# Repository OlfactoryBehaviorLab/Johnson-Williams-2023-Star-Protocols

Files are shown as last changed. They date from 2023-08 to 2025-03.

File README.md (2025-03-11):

# Protocol for Quantifying the Odor Detection Threshold of Mice
# Johnson and Williams, et al., 2023


## https://star-protocols.cell.com/protocols/3043
Scripts and Design files required for the protocol described in the Johnson and Williams, et al., 2023 publication in STAR Protocols

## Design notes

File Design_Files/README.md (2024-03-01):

# 2D and 3D Designs for the Dewan Lab

OdorPort

Collection of 2D and 3D designs for custom components used in the Olfactory Behavior Lab at Florida State University.

3D Files are supplied as stl files for 3D printing purposes.
2D files are supplied as PDF part drawings. Any components not 3D printed will lack an associated stl file. The materials for those 2D drawings are descibed in [Johnson and Williams, 2023](https://star-protocols.cell.com/protocols/3043)

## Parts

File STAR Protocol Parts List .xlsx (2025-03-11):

Part | Discription | Part number | Manufacture # | Vendor | Manufacture
RIG
Rig Frame | ** | ** |  | 80 / 20
Water Custom Panels | ** | ** |  | FRED &TANG
Flow Meter Custom Panels | ** | ** |  | FRED &TANG
Flow Meter Custom Panels | ** | ** |  | FRED &TANG
Flow Meter 10--Vaccuum | AVANTOR MASTERFLEX (VWR LLC) Masterflex Variable-Area Flowmeter with Valve, Direct Reading, Aluminum Fittings, 150-mm Scale; 10 LPM Air | 50-196-1140 | MFLX32003-14 | Fisher Scientific | AVANTOR MASTERFLEX
Flow Meter 2.5 w/ knob--clean air | AVANTOR MASTERFLEX (VWR LLC) Masterflex Variable-Area Flowmeter with Valve, Direct Reading, Brass Fittings, 150-mm Scale; 2.5 LPM Air | 50-196-1143 | MFLX32004-10 | Fisher Scientific | AVANTOR MASTERFLEX
Flow Meter 2.5 w/o know--exhaust | Masterflex® Variable-Area Flowmeter without Valve, Direct-Reading, Brass Fittings, 150-mm Scale; 2.5 L/min Air | MFLX32001-10 | MFLX32001-10 | Avantor (VWR) | AVANTOR MASTERFLEX
1/4 in Female Connectors NPT | Female Adapter: Nylon, Push-to-Connect x FNPT, For 1/4 in Tube OD, 1/4 in Pipe Size, Black, 10 PK | 1PEL6 | 3014 56 14 | Grainger
1/4 in tubing--blue | 5/32″ ID x 1/4″ OD, 3/64″ Wall Thickness, Cut to Length (1000' Standard Length) Polyurethane Tube Blue, 123 Max psi, 95 Hardness | 48651442 | PT0404-1000B | MSC | COILHOSE PNEUMATICS
1/4 in tubing--red | 5/32″ ID x 1/4″ OD, 3/64″ Wall Thickness, Cut to Length (1000' Standard Length) Polyurethane Tube | 48651681 | PT0404-1000TR | MSC | COILHOSE PNEUMATICS
1/4 in tubing--black | 5/32″ ID x 1/4″ OD, 3/64″ Wall Thickness, Cut to Length (1000' Standard Length) Polyurethane Tube Black, 123 Max psi, 95 Hardness | 48651509 | PT0404-1000K | MSC | COILHOSE PNEUMATICS
1/4 in tubing--yellow | GRAINGER APPROVED Tubing: Polyurethane, ID 5/32 in, OD 1/4 in, 100 ft Lg, Yellow | 1CTG5 | 1CTG5 | Grainger
1/8 in tubing--blue | 1/16″ ID x 1/8″ OD, 1/32″ Wall Thickness, Cut to Length (2,500' Standard Length) Polyethylene Tube Blue, 150 Max psi | 48655187 | PE021-2500B | MSC | COILHOSE PNEUMATICS
1/8 in tubing--black | 3/32″ ID x 1/8″ OD, 1/64″ Wall Thickness, Cut to Length (500' Standard Length) Nylon 11 Tube Black, 852 Max psi, 78 Durometer Hardness | 74203712 | 36004 | MSC
1/4 in Y connector PTC | Wye Union: Nylon, Push-to-Connect x Push-to-Connect x Push-to-Connect, Black, Imperial, 10 PK | 1DDR5 | 3140 56 00 | Grainger
Manual Needle valve 1/4 in PTC | SMC Speed Control Valve: Tube, 1/4 in Valve Port Size, 1/4 in Valve Tube Size, In Valve Flow | 4DGV3 | AS2052F-07 | Grainger
1/4 in Y union PTC | Wye Union: Nylon, Push-to-Connect x Push-to-Connect x Push-to-Connect, Black, Imperial, 10 PK | 1DDR5 | 3140 56 00 | Grainger
vaccuum regualtor | SMC Vacuum Regulator: 1/4 in Vacuum Inlet Size, Push to Connect, 140 lpm Max Flow Rate, IRV | 30J548 | IRV10-N07BG | Grainger
Organic filter | ** |  |  | Fred & TANG
restek filter | Super-Clean Gas Filters Replacement (Charcoal) Hydrocarbons Filter, Ultra High Capacity | 22030 |  | Restek
restek base | Super-Clean Baseplate Single Position Baseplate for One Cartridge Filter, 1/8" Brass Fittings | 22025 |  | Restek
1/8-1/4 in Unqual union PTC connector | Unequal Union: Nylon, Push-to-Connect x Push-to-Connect, For 1/8 in x 1/4 in Tube OD, Black, 10 PK | 1PEW2 | 3106 53 56 | Grainger
HAM-LET Ball Vavle | Ball Valve: 1/4 in Pipe Size, Std, 300 psi CWP Max. Pressure, -40 to 400 F, Toggle Hangle | 3ZVX3 | H-1280-B-N-1/4-A | Grainger
Air and Nitrogne Gauges | Ashcroft 30052.5 Commercial Gauge with Back Connection, 0 to 30 psi, 2-1/2" Dial | EW-68008-03 |  | Cole-Parmer
Air Regulator | SPEEDAIRE Compressed Air Regulator: Brass, 1/4 in NPT, 15 cfm, 400 psi Max Op Pressure, Nonrising | 4ZM06 |  | Grainger
Air Tank Regulator | Airgas Single Stage Brass 0-25 psi General Purpose Cylinder Regulator CGA-590 | Y11215A590-AG |  | AirGas
Nitrogen Tank Regulator | Airgas Single Stage Brass 0-25 psi General Purpose Cylinder Regulator CGA-580 | Y11215A580-AG |  | AirGas
1/4 in NPT to PTC connector | Male Adapter: Brass, Push-to-Connect x MNPT, For 1/4 in Tube OD, 1/8 in Pipe Size, 18 mm Overall Lg | 36X026 | KQ2H07-34AS | Grainger
Vavle and Gauge Custom Panel | ** |  |  | FRED &TANG
1/8 in Equal union PTC connector | Union: Nylon, Push-to-Connect x Push-to-Connect, For 1/8 in x 1/8 in Tube OD, Black, 10 PK | 1PEV2 | 3106 53 00 | Grainger
Zero Dead Space Electronic Needle Vavle | EIVU-Z-ENS | EIVU-Z-ENS |  | Clippard
Zero Dead Space fitting | Headless 1/4-28 Flatbottom Fitting, 1/8" OD | ZDVF-18 |  | Clippard
3 way-dual synchronous soleinoid Valve | Dual 3-way isolation valve | SH360T042 |  | NResearch
OLFACTOMETER
1/8 in elbow fitting connector | Male Elbow: Brass, Push-to-Connect x MNPT, For 1/8 in Tube OD, 1/8 in Pipe Size | 36X076 | KQ2L01-34AS | Grainger
1L/SLPM Mass Flow Controller | Mass Controller, 0 - 1 SLPM, Display | MC-1SLPM-D/5M, 5IN, GAS: Air |  | AliCat
100SCCM Mass Flow Controller | Mass Controller, 0 - 100 SCCM, Display | MC-100SCCM-D/5M, 5IN, GAS: Air |  | AliCat
MFC Power cord-- | Power Adapter - 24 VDC, 1 Amp (Worldwide) | PVPS24U |  | AliCat
custom MFC power cord
barb fitting-- Tygon to Manifold | Barb Fittings Zero Dead Volume | FITM331 |  | NResearch
4 Position, 3 normally close 1 normally open manifold | Nresearch-3 NC, 1 NO 2-way Inline Isolation Valve | 225T081 |  | NResearch
4 Position Normally closed Manifold | 4x2-way NC Inline Isolation Valve | 225T082 |  | NResearch
1/8 in black ferrle/yellow nut | Super Flangeless™ Ferrule Tefzel™ (ETFE), 1/4-28 Flat-Bottom, for 1/8" OD Yellow - 10 Pack | P-359X |  | Idex
big Teflon Tubing | Teflon Tubing .062 in I.D., .125 in O.D., Inert(PTFE) | TBGM110 |  | NResearch
1/8 in Manual Needle Valve PTC
Nitrogen manifold plug | Plug 1/4-28 PTFE | FITM128 |  | NResearch
Two piece fitting set | Two Piece fitting set 1/4-28, 0.36x0.62 PCTFE | 252P109-50 |  | NResearch
small Teflon tubing | Teflon Tubing .036 in I.D., .062 in O.D., Inert(PTFE) | TBGM109 |  | NResearch
Amber Glass Vials
Silicon/Teflon Septum w/ Cap
Teensy to computer Cable
Teensy connector board | PJRC Teensy USB Board with Header Pins |  |  | PJRC
Controller Board
Vial board
Dummy Vial Board
2 Position Jumper Pin | 2 (1 x 2) Position Shunt Connector Black Closed Top 0.100" (2.54mm) Tin | S9000-ND | STC02SYAN | DigiKey | Sullins Connector Solutions
Female Molex Connector | Socket Contact Tin 20-24 AWG Crimp Power | WM1837-ND | 430300007 | DigiKey | Molex
Male Molex Housing | 2 Rectangular Connectors - Housings Receptacle Black 0.118" (3.00mm) | WM1845-ND | 436450200 | DigiKey | Molex
small cable ribbon | CBL RIBN 10COND 0.05 GRAY 5'; Flat Ribbon Cable Gray 10 Conductors 0.050" (1.27mm) Flat Cable 5.0' (1.52m) | MC10G-5-ND | 3365/10 300SF | DigiKey | 3M
small cable ribbon connector | CONN RCPT 10P IDC 26-28AWG GOLD; 10 Position Rectangular Receptacle Connector IDC Gold 26-28 AWG | MKC10A-ND | 89110-0101 | DigiKey | 3M
Power Cable
On/Off Switch
3 in machine screw
Board stand-offs | BRD SPT SNAP LOCK NYLON 1/4" | RP426-ND | LCBS-4-01 | DigiKey | Essentra Components (https://www.digikey.com/en/supplier-centers/essentra-components)
Custom acrylic shield | ** |  |  | FRED &TANG
ARDUINO/COMPUTER
Arduino plastic casing | ** |  |  | FRED&TANG
Arduino custom panel | ** |  |  | FRED&TANG
BNC cable rigs | Connector Nut For BNC and TNC Connectors | A97566-ND | 1-1634816-0 | DigiKey | TE Connectivity AMP Connectors
BNC cable | CBL ASSY BNC PLUG-PLUG RG58C 6'; Cable Assembly Coaxial BNC to BNC RG-58C 72.0" (1.8m) 6.0' | 501-1021-ND | 2249-C-72 | DigiKey | Pomona Electronics (https://www.digikey.com/en/supplier-centers/pomona-electronics)
BNC Cable | CBL ASSY BNC PLUG RG58C 36"; Cable Assembly Coaxial BNC to BNC RG-58C 36.00" (914.40mm) | 501-1018-ND | 2249-C-36 | DigiKey | Pomona Electronics (https://www.digikey.com/en/supplier-centers/pomona-electronics)
ZDS Electronic needle valve Controller Box | ** |  |  | FRED &TANG
4 position black cable | CABLE MOD FLAT 4COND BLACK 100';4 Conductor Modular Straight Cable Black 100' (30.5m) | A0042R-100-ND | AT-K-26-4-B/100 | DigiKey | Assmann WSW Components (https://www.digikey.com/en/supplier-centers/assmann-wsw-components)
LCD Screen Ardunio board | LCD MOD 32DIG 16X2 TRANS YLW/GRN; Character Display Module Transflective 5 x 8 Dots STN - Super-Twisted Nematic LED - Yellow/Green Serial 80.00mm x 36.00mm x 25.50mm | 27977-ND | 27977 | DigiKey | Parallax Inc. (https://www.digikey.com/en/supplier-centers/parallax)
small single pin wires with housing |  |  |  |  | Polulo
Arduino Board | ARDUINO MEGA2560 ATMEGA2560; ATmega2560 Arduino Mega2560 AVR® ATmega AVR MCU 8-Bit Embedded Evaluation Board | 1050-1018-ND | A000067 | DigiKey | Arduino (https://www.digikey.com/en/supplier-centers/arduino)
Arduino power? | AC/DC WALL MOUNT ADAPTER 12V 12W | 102-3432-ND | SWI12-12-N-P6 | DigiKey | CUI Inc. (https://www.digikey.com/en/supplier-centers/cui)
Arduino to computer cable
Breakout Board | 2x20 0.1" Header IDC40 Breakout Board | BRK2X20-L-DIN |  | Winford
wiring | ** |  |  | FRED&TANG
40 position ribbon Cable | IDC CBL - HHKC40S/AE40G/HHKC40S; 40 Position Cable Assembly Rectangular Socket to Socket 3.00' (914.40mm) | H3CCS-4036G-ND | H3CCS-4036G | DigiKey | Assmann WSW Components (https://www.digikey.com/en/supplier-centers/assmann-wsw-components)
#2-56 nut | Hex Nut: #2-56 Thread, 3/16 in Hex Wd, 1/16 in Hex Ht, Steel, Not Graded, Zinc Plated, 100 PK (https://www.grainger.com/product/GRAINGER-APPROVED-Hex-Nut-2-56-Thread-2FE43) | 2FE43 | 325040-PG | Grainger
BEHAVIORAL BOX
Lick ciruit board
#2 mechanical screw 1/2 in | #2-56 Machine Screw, Carbon Steel, 1/2" L, 100 PK | 1ME91 |  | Grainger
metal lick tube
dental wax | Utility Wax Strips HSI Round White 64/Bx | 1008759 |  | Henry Schein
tygon tubing--lick tubes | Tubing: Tygon S3 E-3603, TPE, 1/32 in Inside Dia, 3/32 in Outside Dia, 50 ft Lg, Clear | 22XH28 | ACF00001 | Grainger
60 mL syringe | SYRINGE LUER LOCK 60CC CS100 | 15003-094 | SS-60L | VWR | TERUMO MEDICAL INC. (https://us.vwr.com/store/supplier/id/0000020530/terumo-medical-inc.)
needle to water solinoid connection | Cole-Parmer Adapter, PP, Male Luer Lock to 10-32 thread, 25/pack | EW-45518-84 |  | Cole-Parmer
blunted interlocking needle 21 GA | Blunt Tip Needles with Dispensing Tips, Air-Tite | 89500-304 | NB2112 | VWR | AirTite
water solienoid | 2-way NC Isolation Valve | 161T012 |  | Nresearch
angle bracket micromanipulator | DT100-AB; angle bracket, DT-100 series | 60050000E |  | Siskiyou
micromanipulator | DT3-100; dovetail stage, 12mm travel, XYZ | 62080000E |  | Siskiyou
vaccuum/mfc tygon tubing | Tubing: Tygon S3 B-44-3, TPE, 1/8 in Inside Dia, 3/16 in Outside Dia, 50 ft Lg, Clear | 2LPR9 | AAB00006 | Grainger
barb to NPT--tygon vaccuum to flowmeter | 1/8″ Barb, 1/8 NPT, Nylon Single Barbed Tube Adapter | 48712244 | A2-2BN | MSC
1/2 in pedestal | Ø1" (Ø25.0 mm) Pedestal Posts, 1/4"-20 (M6) Taps | RS05P |  | Thorlabs
pedastal clamp | CF125-P5 - Clamping Fork, 1.24" Counterbored Slot, Universal, 5 Pack | CF125-P5 |  | Thorlabs
Magnetic Base (Top and Bottom) | Complete 3" x 3" Kinematic Base, Top and Bottom Plates, 1/4"-20 Mounting | KB3X3 |  | ThorLabs
Bread Board 12x12 | Aluminum Breadboard 12" x 12" x 1/2", 1/4"-20 Taps | MB12 |  | ThorLabs
light bulb | LED WHITE CLEAR T-1 T/H; White LED Indication - Discrete 12V Radial | LTH3MM12VFR4400-ND | LTH3MM12VFR4400 | DigiKey | Visual Communications Company - VCC (https://www.digikey.com/en/supplier-centers/visual-communications-company)
4 in optical post | 1/2" Optical Post, SS, 8-32 Setscrew, 1/4"-20 Tap, L = 4" | TR4 |  | Thorlabs
2 in pedestal | Ø1" (Ø25.0 mm) Pedestal Posts, 1/4"-20 (M6) Taps | RS2P |  | ThorLabs
Webcam | Generic U19-A Night Vision Webcam 12.0MP, Microphone Built In | JUF4645 |  | Amazon
1/4-20 screw inserts | Knurled Press Insert: Flanged, 1/4-20 Internal Thread Size, 1/2 in Lg, 5/16 in Drill Size, 25 PK | 4ZU39 |  | Grainger
thumb screw inserts | GRAINGER APPROVED Press Insert: Brass, 4-40 Internal Thread Size, 3/16 in Lg, 50 PK | 1GUC6 |  | Grainger
headbar clamps
headbar clamp pin
thumb screw | Thumb Screw: #4-40 Thread Size, Knurled, 18-8 Stainless Steel, Plain, 0.094 in Max Head Ht | 5RA21 | Z2300SS | Grainger
custom headbar
Teflon Odor Port | JF-DR-OP0008 Odor Port, Top |  |  | Max Plank Neuroscience
#2 mechanical screw 3/4 in | #2-56 Machine Screw, Carbon Steel, 3/4" L, 100 PK | 1ME92 |  | Grainger
exhaust fan | FAN AXIAL 80X25.4MM 12VDC WIRE | 381-2335-ND
sound proofing foam | Quiet Barrier® Specialty Composite: 1 1/4 in. thick x 48 in. x 54 in. sheet with PSA |  |  | Soundproof Cow
custom acrylic base plate | ** |  |  | FRED&TANG
1/4-20 set screw | HW-KIT2 - 1/4"-20 Cap Screw and Hardware | HW-KIT2 |  | ThorLabs
#4-40 nut for set screw small | Hex Nut: #4-40 Thread, 1/4 in Hex Wd, 3/32 in Hex Ht, Steel, Not Graded, Zinc Plated, 100 PK (https://www.grainger.com/product/GRAINGER-APPROVED-Hex-Nut-4-40-Thread-2GA51) | 2GA51 | 325080-PG | Grainger
CLEANING
Surgery
screws for head-bar surgeries |  | 000-120 X 1/16th inch | AMS120-1B-25 | Antrin Miniature Specialties
heat therapy pump |  |  | HTP1500 | Kent scientific

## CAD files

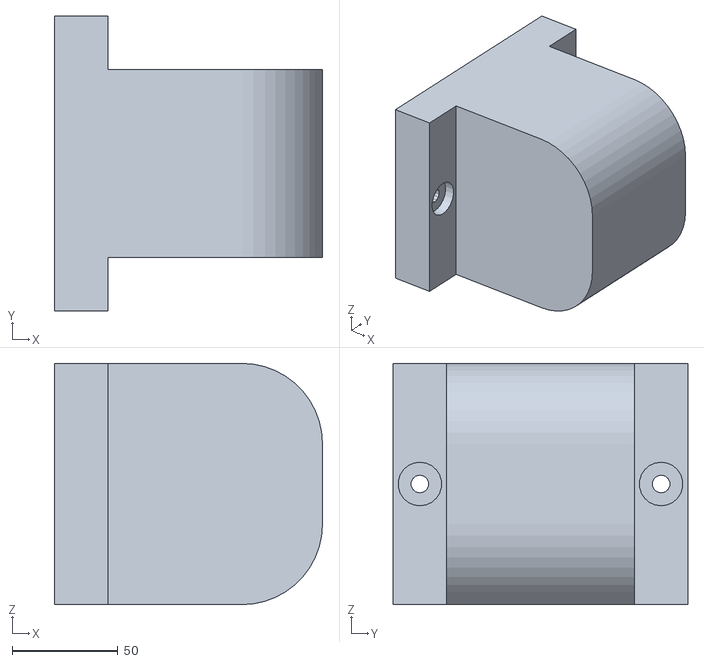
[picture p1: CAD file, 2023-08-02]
Design_Files/Behavioral_Rig_Components/Cleaning_Bottle_Holder/Cleaning Bottle Holder.stl
127.0 x 139.7 x 114.3

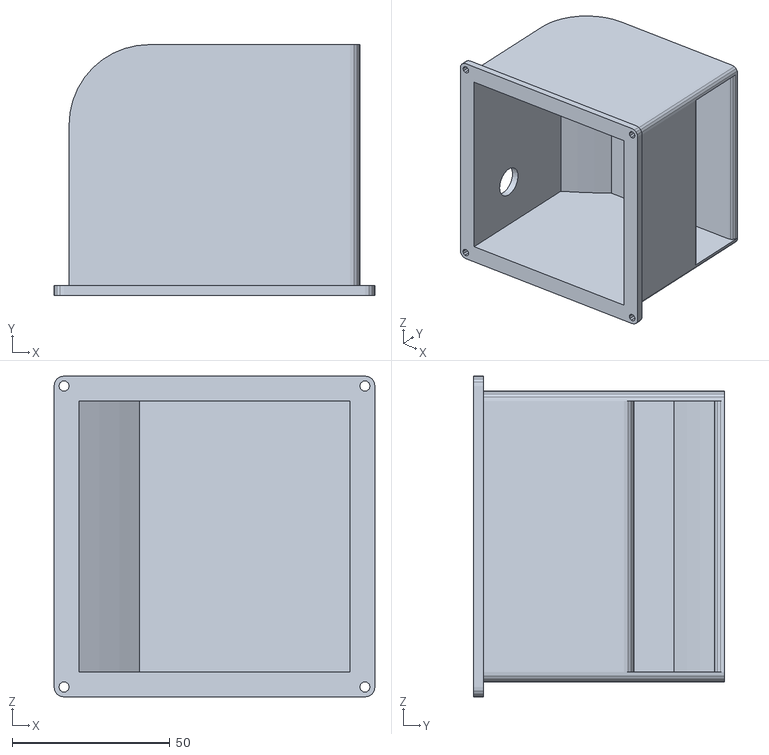
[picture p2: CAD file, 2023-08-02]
Design_Files/Behavioral_Rig_Components/Fan_Exhaust_Cover/FanExhaustCover.stl
101.6 x 79.4 x 101.6

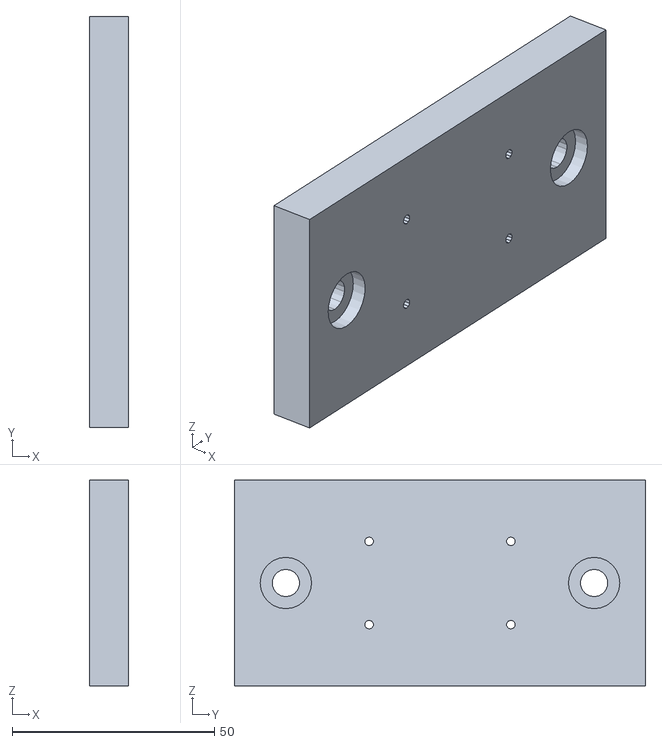
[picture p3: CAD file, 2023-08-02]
Design_Files/Behavioral_Rig_Components/FinalValve_Mount/FinalValveMount.stl
9.52 x 101.6 x 50.8

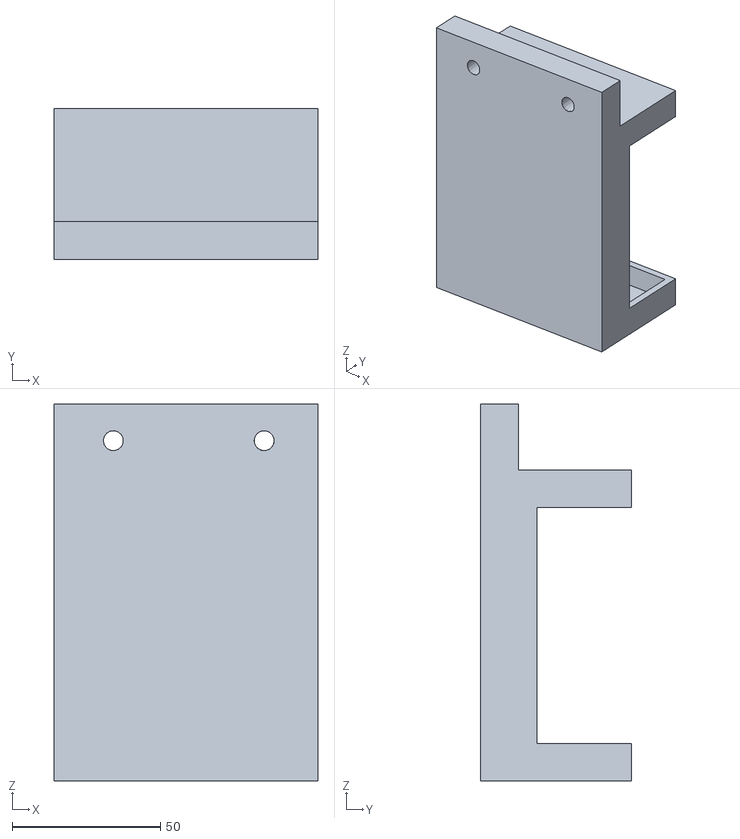
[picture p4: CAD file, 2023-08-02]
Design_Files/Behavioral_Rig_Components/KVM_Holder/KVM Holder RMount.stl
88.9 x 50.8 x 127.0

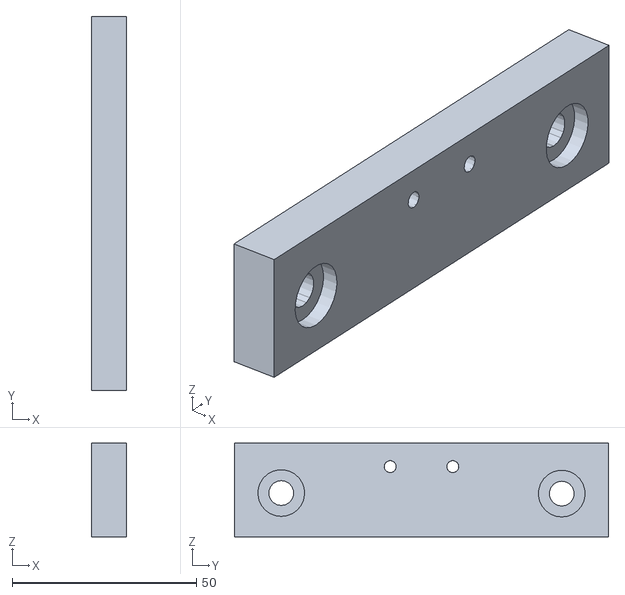
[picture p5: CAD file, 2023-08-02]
Design_Files/Behavioral_Rig_Components/Manual_NeedleValve_Mount/ManualNeedleValveMount.stl
9.52 x 101.6 x 25.4

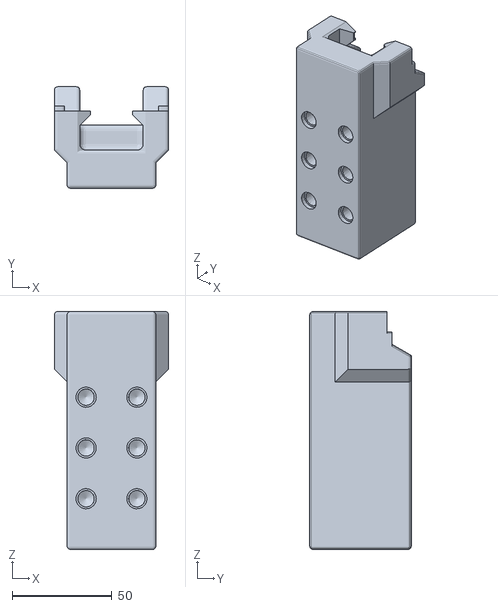
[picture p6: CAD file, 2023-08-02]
Design_Files/Behavioral_Rig_Components/Mouse_Holder/mouse holder.stl
57.2 x 50.8 x 119.1

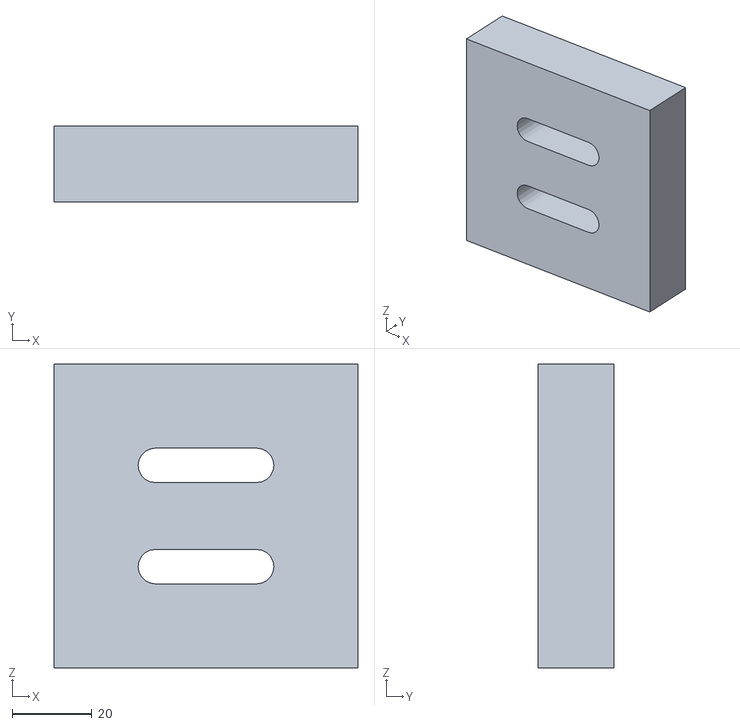
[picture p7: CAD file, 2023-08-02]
Design_Files/Behavioral_Rig_Components/Mouse_Holder_Riser/Mouse Holder Riser.stl
76.2 x 19.0 x 76.2

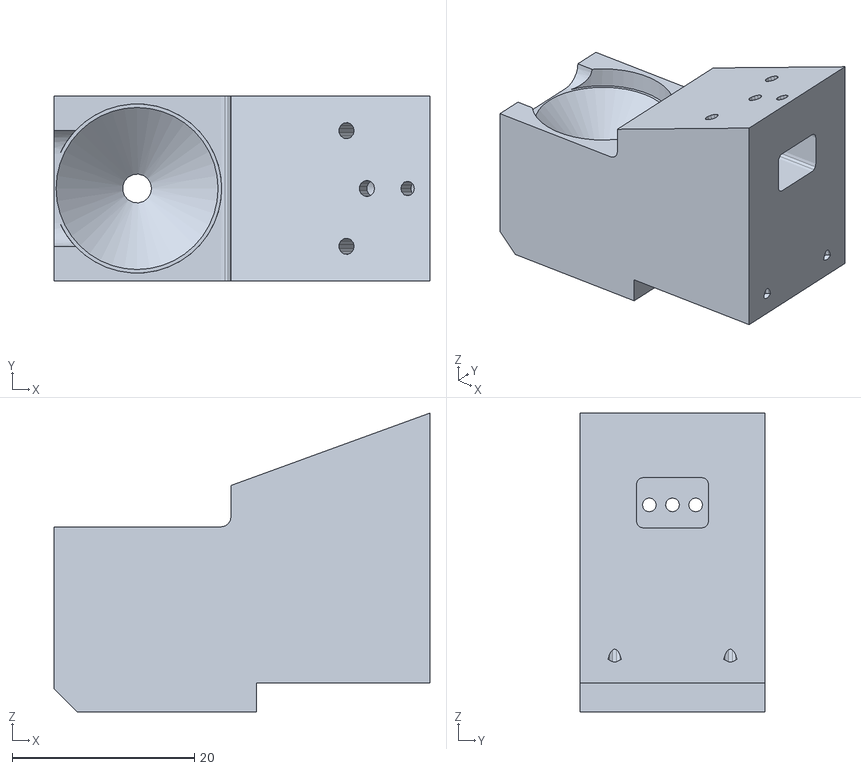
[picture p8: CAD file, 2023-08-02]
Design_Files/Behavioral_Rig_Components/Odor_Port_Base/Odor Port Base.stl
41.3 x 20.3 x 32.8

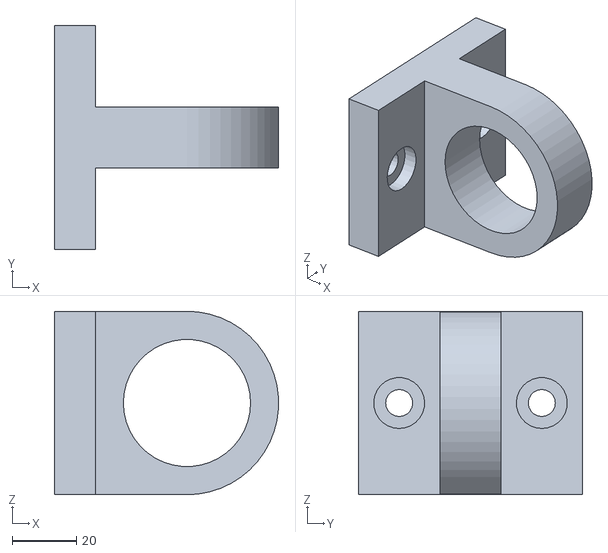
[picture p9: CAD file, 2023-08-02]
Design_Files/Behavioral_Rig_Components/Organic_Filter_Holder/Organic Filter Holder.stl
69.8 x 69.8 x 57.2

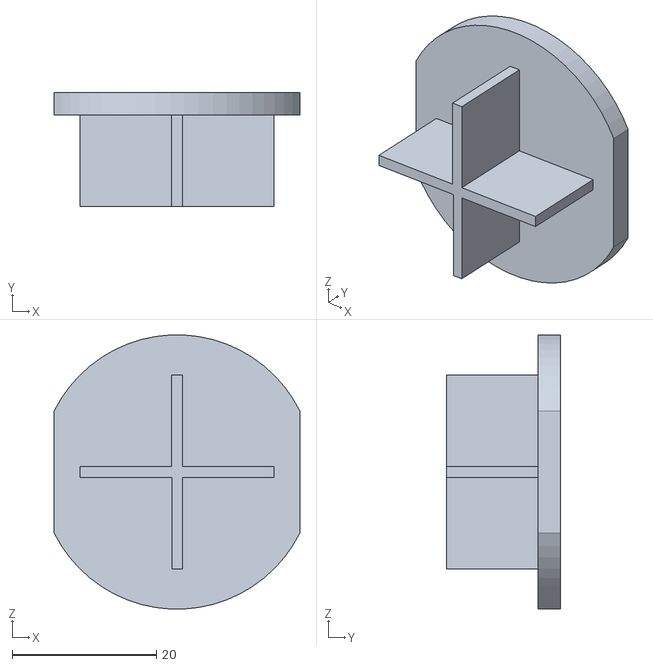
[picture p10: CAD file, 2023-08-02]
Design_Files/Behavioral_Rig_Components/Water_Syringe_Cap/Water Syringe Cap.stl
34.1 x 15.9 x 38.0

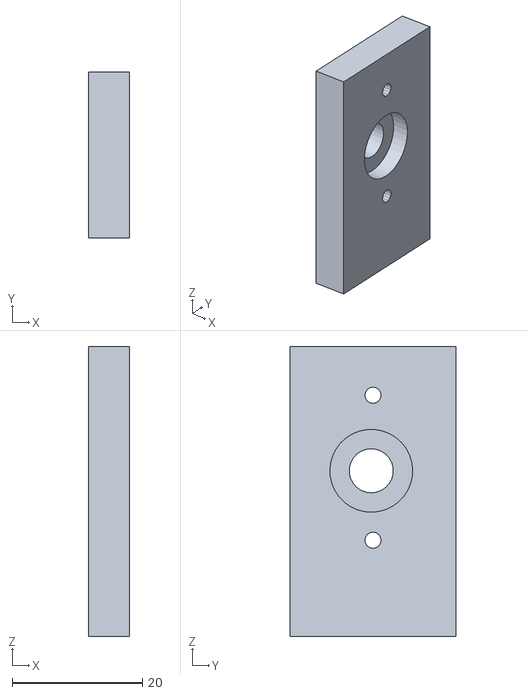
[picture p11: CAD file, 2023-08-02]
Design_Files/Behavioral_Rig_Components/ZeroDeadSpace_ElectronicNeedleValve_Panel/Zero Dead Space Electronic needle valve holder.stl
6.35 x 25.4 x 44.5

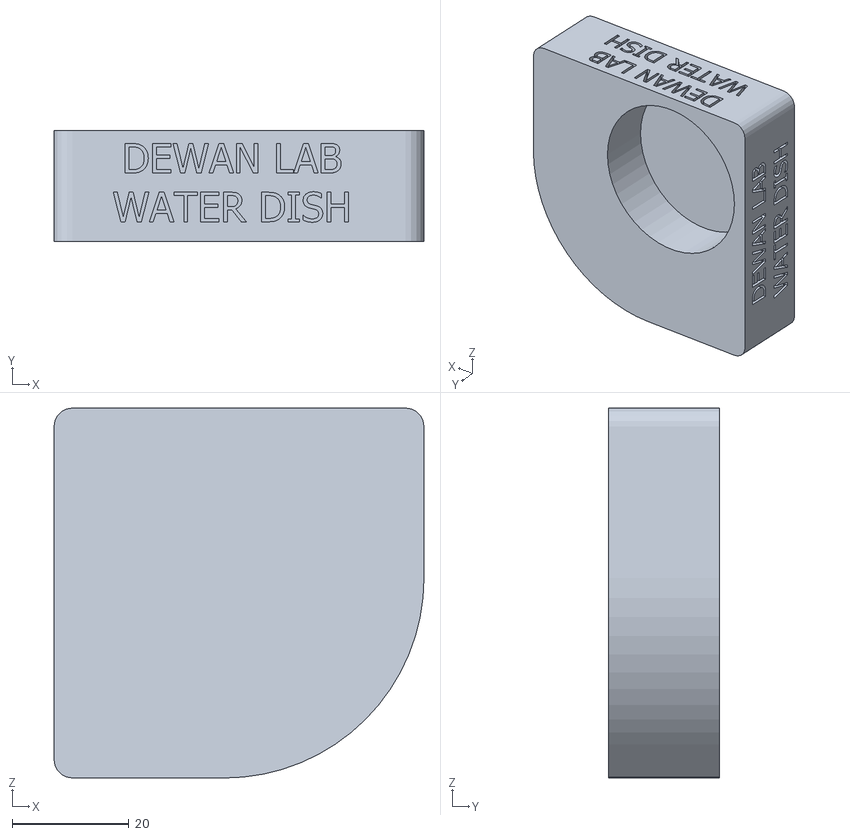
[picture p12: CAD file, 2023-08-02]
Design_Files/General_Components/Water_Dish_Holder/water dish holder.stl
63.5 x 19.0 x 63.5

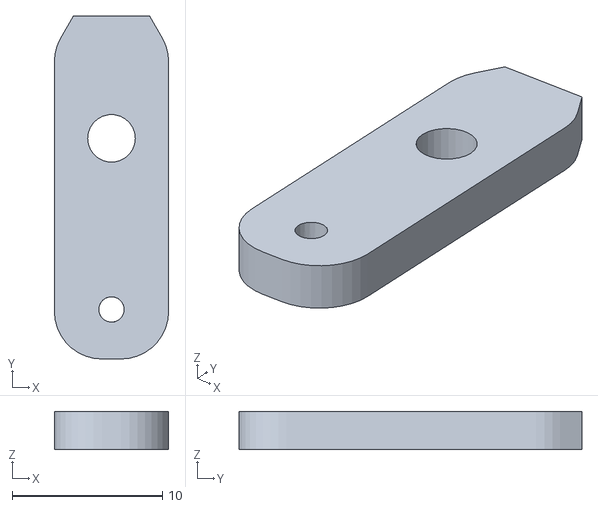
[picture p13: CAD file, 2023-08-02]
Design_Files/Headbar_Components/HEADBAR CLAMP/Headbar clamp.stl
7.62 x 22.9 x 2.54

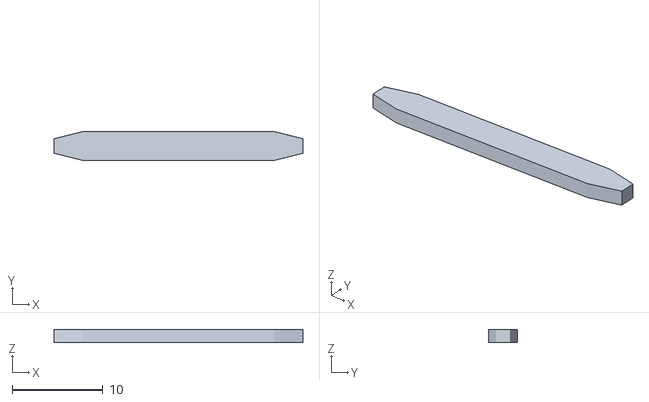
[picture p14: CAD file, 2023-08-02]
Design_Files/Headbar_Components/HEADBAR/Head Bar.stl
27.4 x 3.17 x 1.40

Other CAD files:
Design_Files/Olfactometer_Components/Olfactometer_Manifold_Holder/Olfactometer Manifold Holder.stl
Design_Files/Olfactometer_Components/Olfactometer_Vial_Holder/Vial Holder 4 spaces.stl
Design_Files/Behavioral_Rig_Components/KVM_Holder/KVM Holder LMount.stl
Design_Files/Behavioral_Rig_Components/Mouse_Holder/mouse holder cover.stl
Design_Files/Behavioral_Rig_Components/Odor_Port_Base/Odor Port Base_Side Version.stl

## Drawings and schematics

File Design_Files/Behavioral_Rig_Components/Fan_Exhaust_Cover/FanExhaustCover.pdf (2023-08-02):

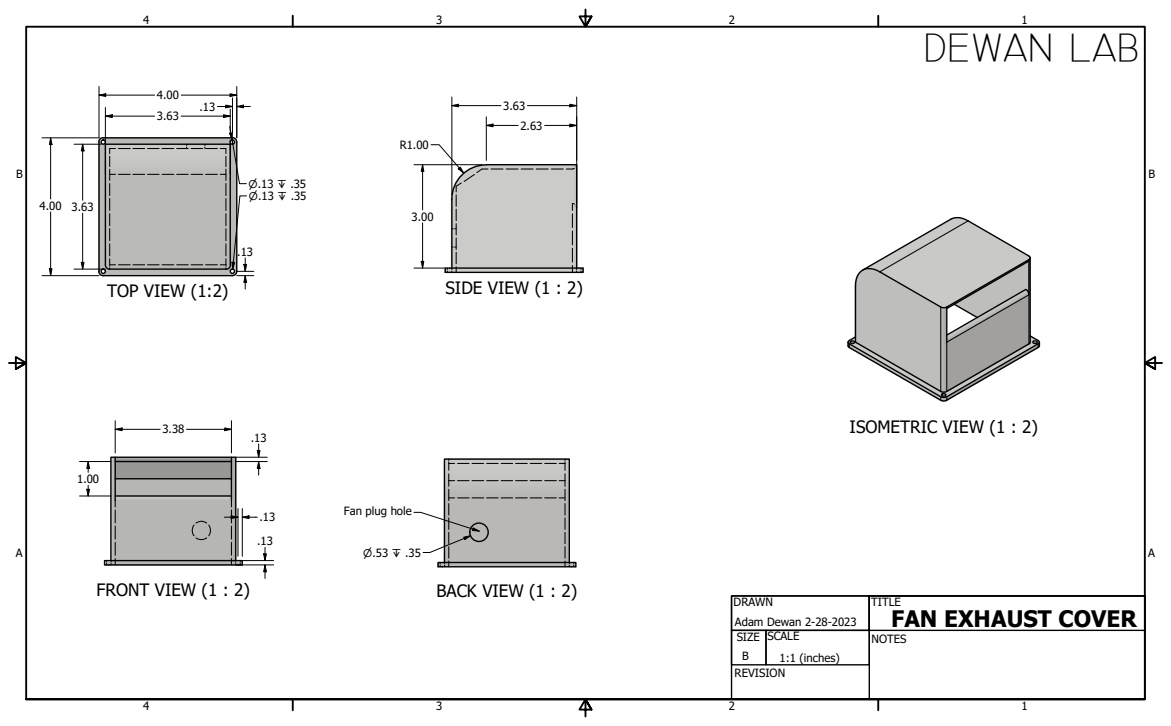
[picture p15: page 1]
TOP VIEW (1:2); SIDE VIEW (1 : 2); FRONT VIEW (1 : 2); BACK VIEW (1 : 2); ISOMETRIC VIEW (1 : 2); DEWAN LAB

Fan plug hole

DRAWN Adam Dewan 2-28-2023 | TITLE FAN EXHAUST COVER

SIZE B | SCALE 1:1 (inches) | NOTES

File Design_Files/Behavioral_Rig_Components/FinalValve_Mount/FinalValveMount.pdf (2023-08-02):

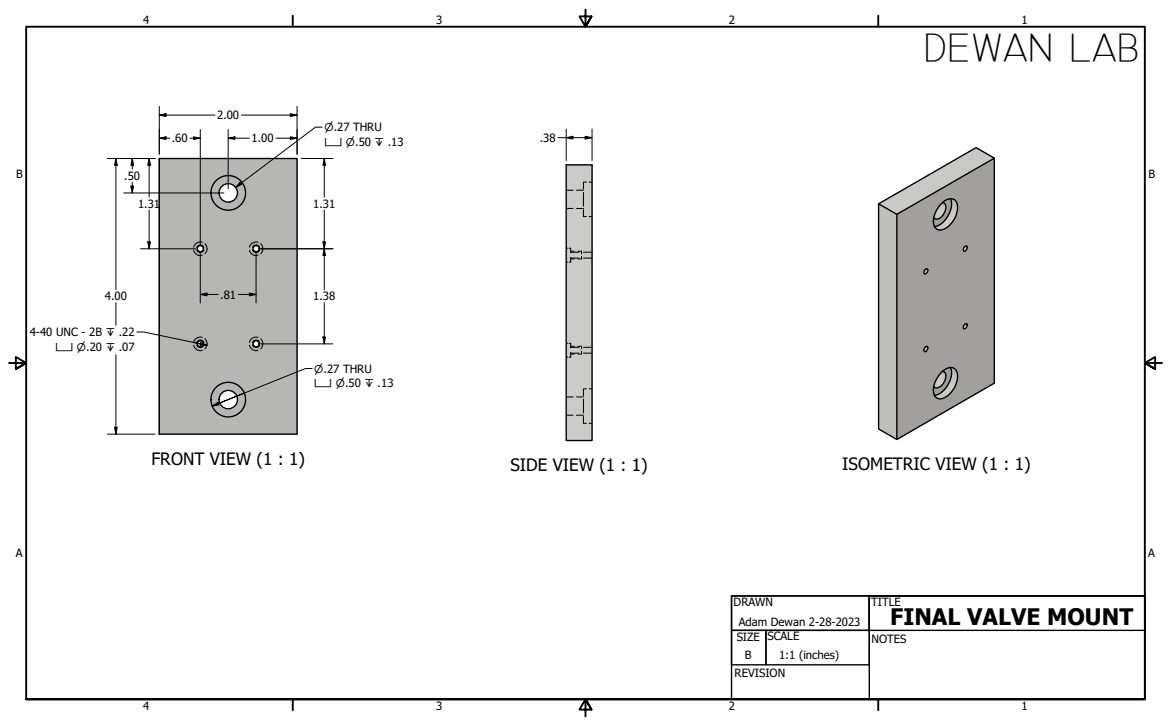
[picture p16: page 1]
FRONT VIEW (1 : 1); SIDE VIEW (1 : 1); ISOMETRIC VIEW (1 : 1); DEWAN LAB; ⌀.27 THRU ⌴ ⌀.50 ↧ .13; 4-40 UNC - 2B ↧ .22 ⌴ ⌀.20 ↧ .07

DRAWN Adam Dewan 2-28-2023 | TITLE FINAL VALVE MOUNT

SIZE B | SCALE 1:1 (inches) | NOTES

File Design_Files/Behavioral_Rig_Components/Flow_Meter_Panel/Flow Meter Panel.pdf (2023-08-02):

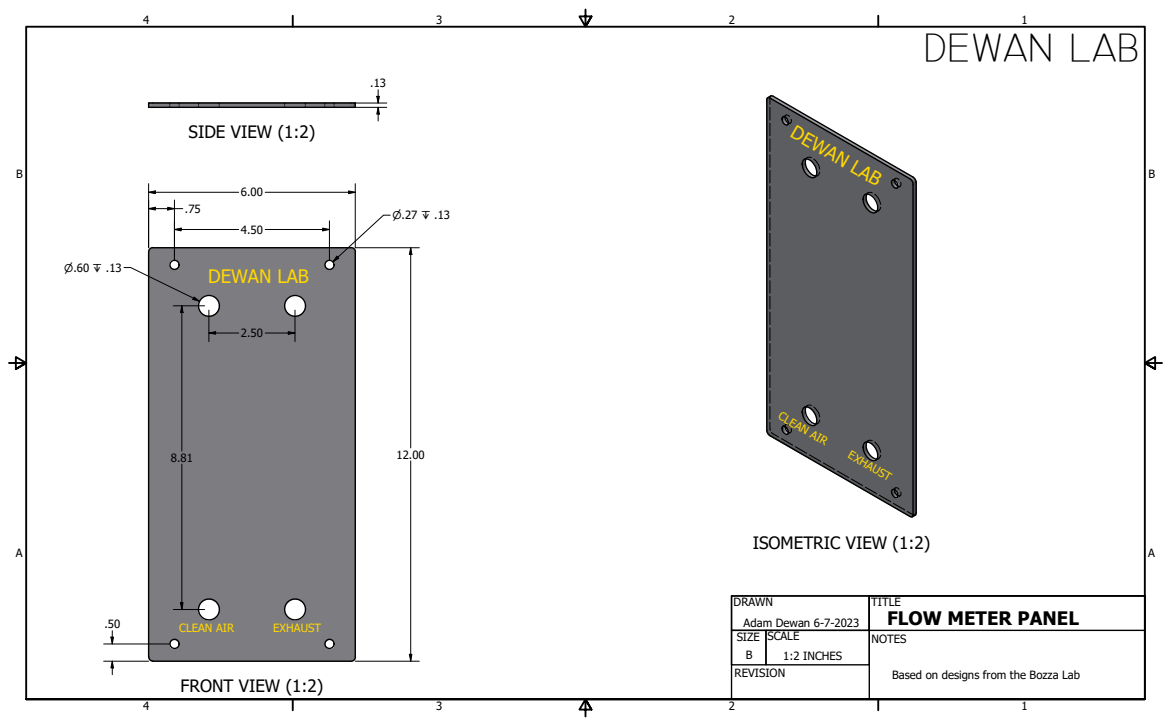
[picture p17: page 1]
SIDE VIEW (1:2); FRONT VIEW (1:2); ISOMETRIC VIEW (1:2); DEWAN LAB; CLEAN AIR; EXHAUST

DRAWN Adam Dewan 6-7-2023 | TITLE FLOW METER PANEL

SIZE B | SCALE 1:2 INCHES | NOTES Based on designs from the Bozza Lab

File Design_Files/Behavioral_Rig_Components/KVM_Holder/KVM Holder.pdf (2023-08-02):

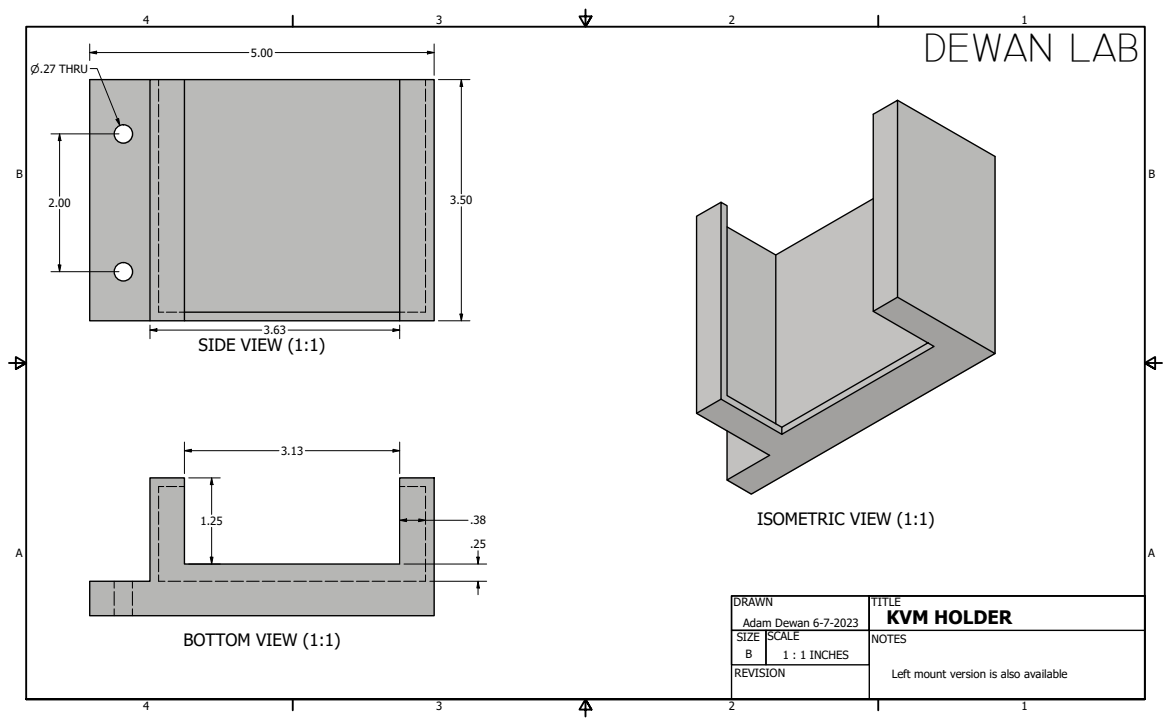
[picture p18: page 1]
SIDE VIEW (1:1); BOTTOM VIEW (1:1); ISOMETRIC VIEW (1:1); DEWAN LAB; ⌀.27 THRU

DRAWN Adam Dewan 6-7-2023 | TITLE KVM HOLDER

SIZE B | SCALE 1 : 1 INCHES | NOTES Left mount version is also available

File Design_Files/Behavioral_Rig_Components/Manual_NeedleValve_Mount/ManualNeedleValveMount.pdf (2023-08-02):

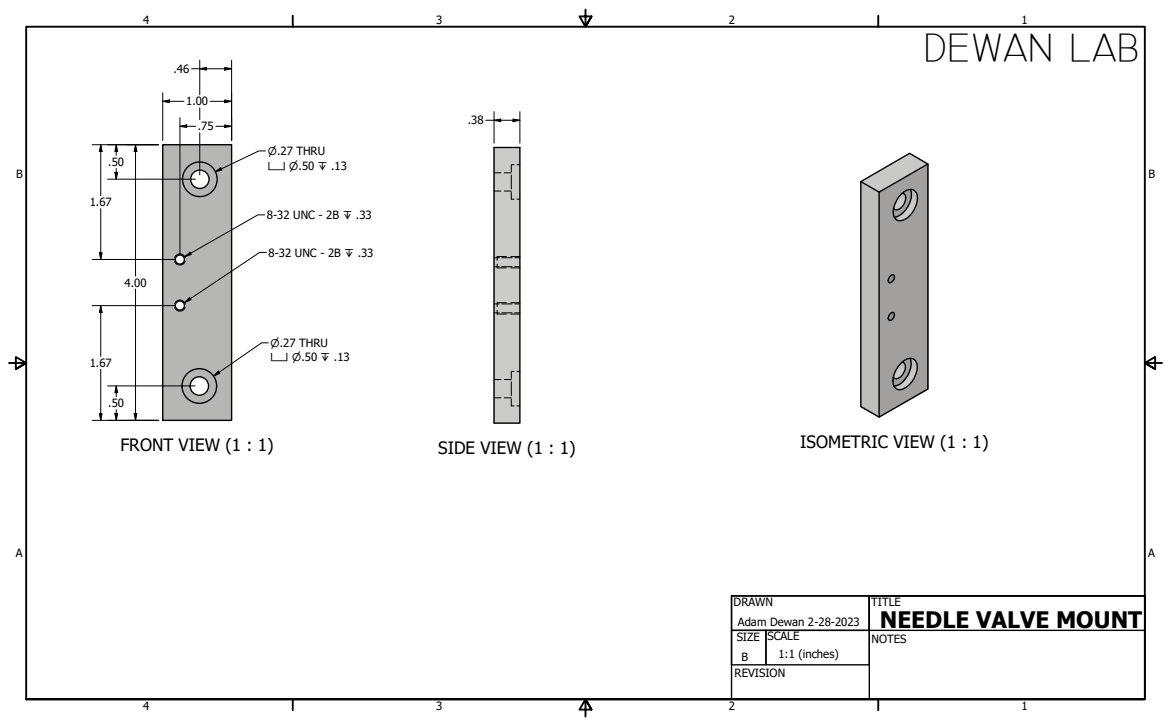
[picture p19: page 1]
FRONT VIEW (1 : 1); SIDE VIEW (1 : 1); ISOMETRIC VIEW (1 : 1); DEWAN LAB; ⌀.27 THRU ⌴ ⌀.50 ↧ .13; 8-32 UNC - 2B ↧ .33

DRAWN Adam Dewan 2-28-2023 | TITLE NEEDLE VALVE MOUNT

SIZE B | SCALE 1:1 (inches) | NOTES

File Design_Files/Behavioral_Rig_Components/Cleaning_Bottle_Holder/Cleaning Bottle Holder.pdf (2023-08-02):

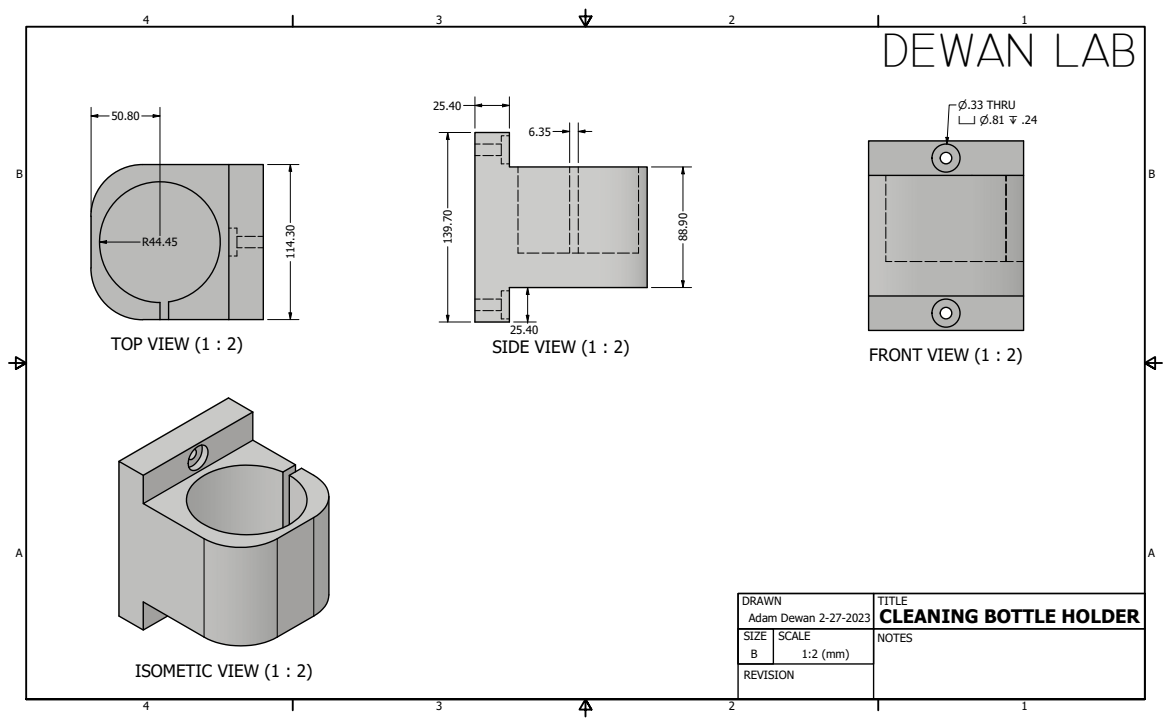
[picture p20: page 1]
TOP VIEW (1 : 2); SIDE VIEW (1 : 2); FRONT VIEW (1 : 2); ISOMETIC VIEW (1 : 2); ⌀.33 THRU ⌴ ⌀.81 ↧ .24; DEWAN LAB

DRAWN Adam Dewan 2-27-2023 | TITLE CLEANING BOTTLE HOLDER

SIZE B | SCALE 1:2 (mm) | NOTES

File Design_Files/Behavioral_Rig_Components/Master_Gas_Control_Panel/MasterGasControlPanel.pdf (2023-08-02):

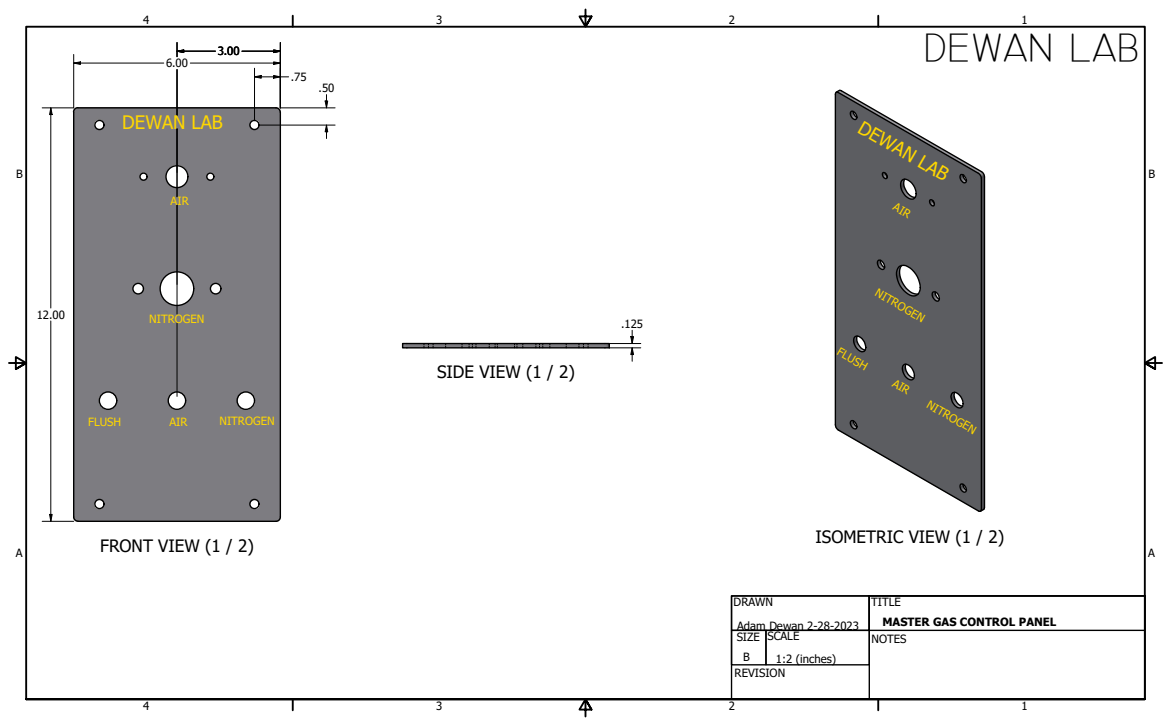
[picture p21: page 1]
FRONT VIEW (1 / 2); SIDE VIEW (1 / 2); ISOMETRIC VIEW (1 / 2); DEWAN LAB

DRAWN Adam Dewan 2-28-2023 | TITLE MASTER GAS CONTROL PANEL

SIZE B | SCALE 1:2 (inches) | NOTES

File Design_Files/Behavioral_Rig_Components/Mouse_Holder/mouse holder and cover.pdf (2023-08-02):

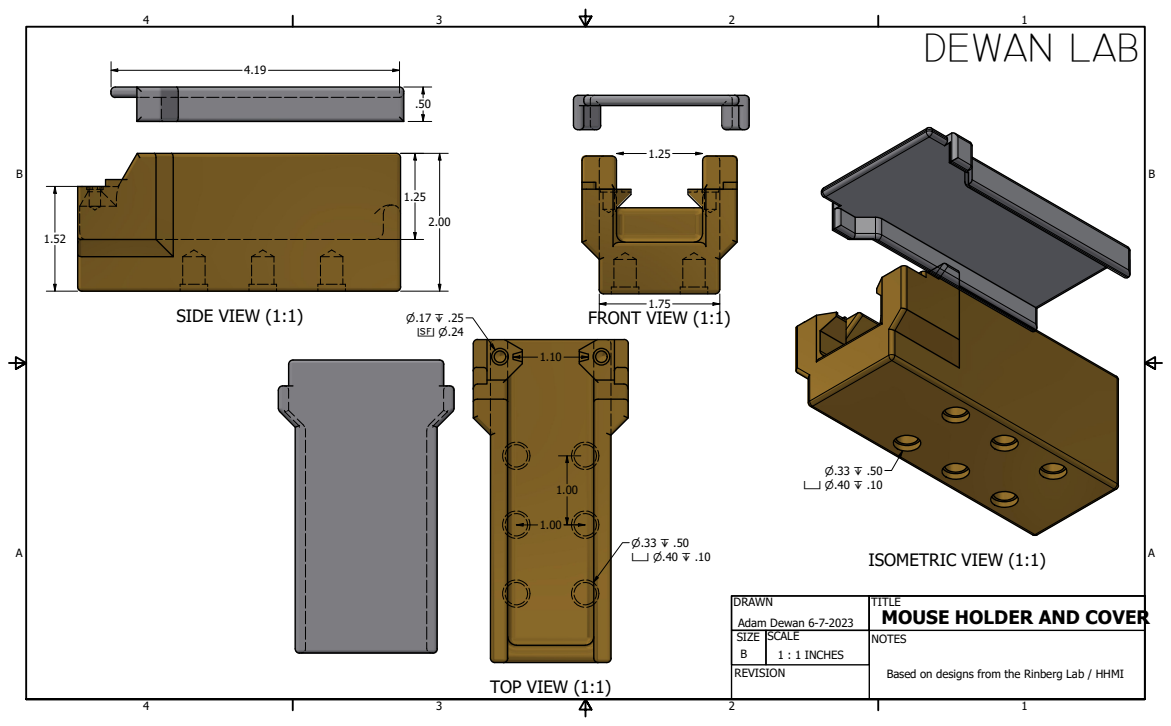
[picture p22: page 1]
SIDE VIEW (1:1); TOP VIEW (1:1); FRONT VIEW (1:1); ISOMETRIC VIEW (1:1); DEWAN LAB; Adam Dewan 6-7-2023; MOUSE HOLDER AND COVER

DRAWN | TITLE

SIZE B | SCALE 1 : 1 INCHES | NOTES Based on designs from the Rinberg Lab / HHMI

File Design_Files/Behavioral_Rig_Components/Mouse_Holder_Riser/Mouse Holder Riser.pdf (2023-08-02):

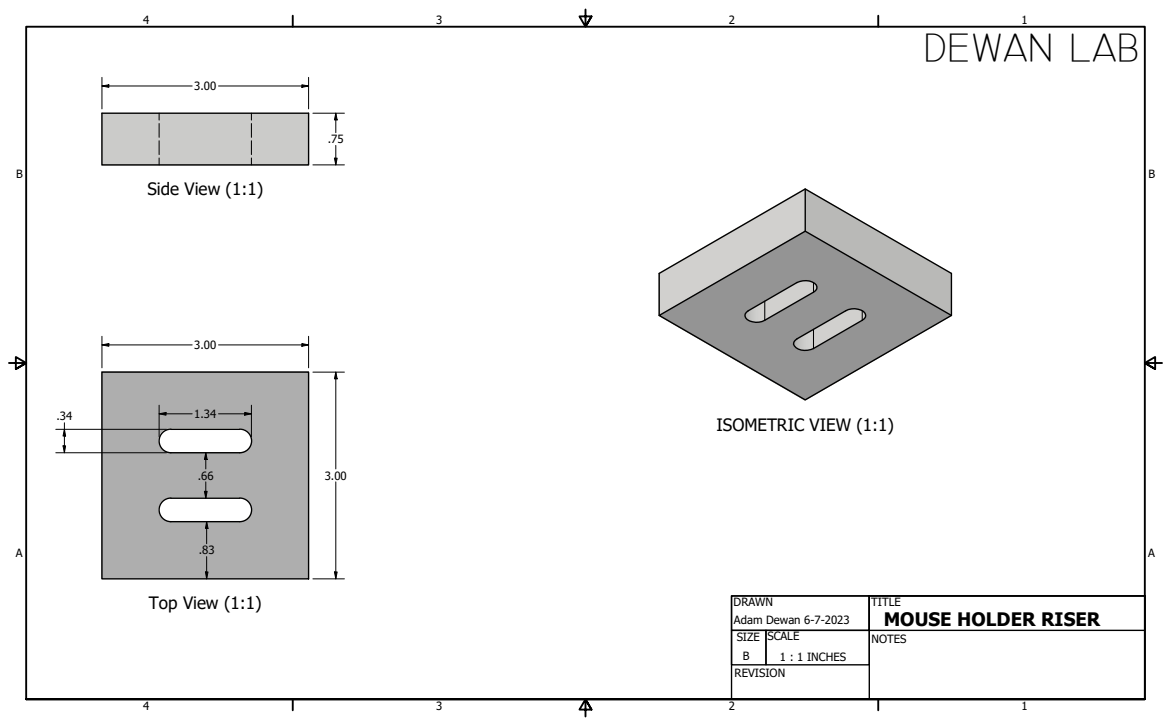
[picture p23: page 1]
Side View (1:1); Top View (1:1); ISOMETRIC VIEW (1:1); DEWAN LAB

DRAWN Adam Dewan 6-7-2023 | TITLE MOUSE HOLDER RISER

SIZE B | SCALE 1 : 1 INCHES | NOTES

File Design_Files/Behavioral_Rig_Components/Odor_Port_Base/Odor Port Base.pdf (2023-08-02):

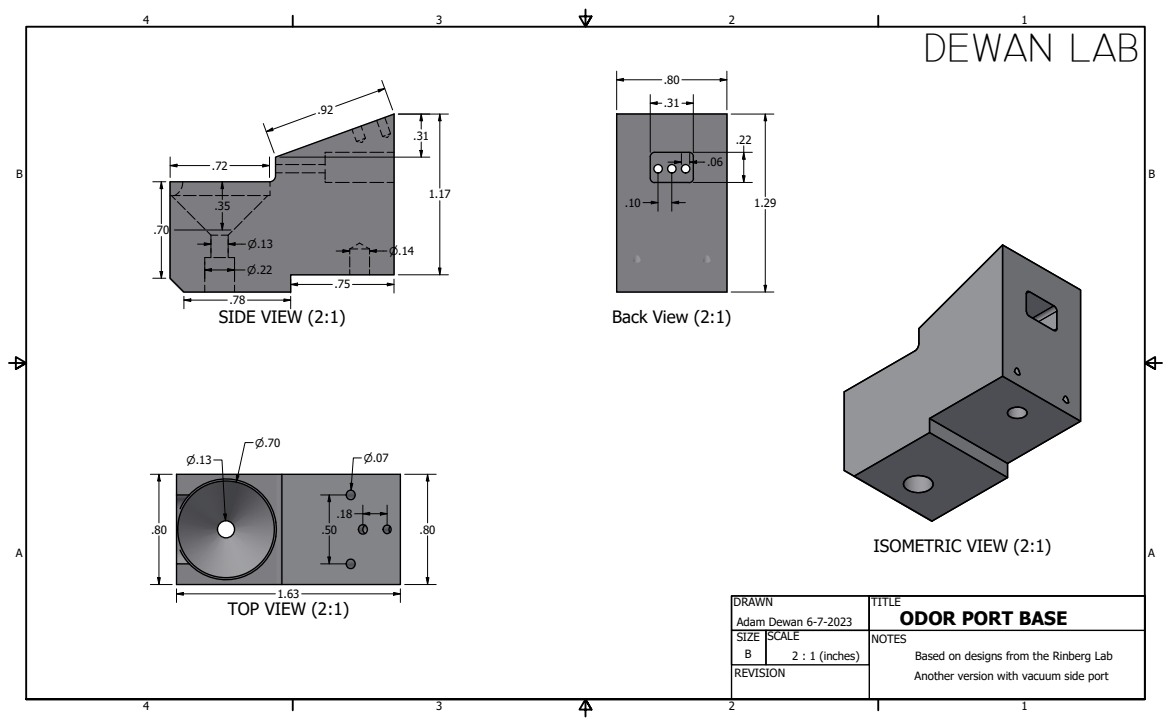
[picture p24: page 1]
SIDE VIEW (2:1); TOP VIEW (2:1); Back View (2:1); ISOMETRIC VIEW (2:1); DEWAN LAB

DRAWN Adam Dewan 6-7-2023 | TITLE ODOR PORT BASE

SIZE B | SCALE 2 : 1 (inches) | NOTES Based on designs from the Rinberg Lab Another version with vacuum side port

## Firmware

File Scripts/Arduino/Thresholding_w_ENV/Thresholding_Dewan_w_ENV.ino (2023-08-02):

// include the library code:
#include <SPI.h>
#include <C:\Voyeur_protocols_and_files\Arduino\libraries\voyeur_timer_lib.pde>
#include <C:\Voyeur_protocols_and_files\Arduino\libraries\ioFunctions_external_timers.pde>
#include <C:\Voyeur_protocols_and_files\Arduino\libraries\voyeur_serial_stream_tools.pde>
#include <C:\Voyeur_rig_config\arduino_rig_config.h>

#define INITIALGO 0
#define GO 1
#define NOGO 2

#define PASSIVE 4
#define PASSIVEREWARDED 3
#define POSITIVE 1
#define NEGATIVE 0
#define FV 3
#define TRIAL_LED CUE3
#define THREEMISSED_LED CUE4
#define FVSYNC DIGITAL7

//=======================
// Set the protocol name
char protocolName[] = "ThresholdingENV"; // should be less than 20 characters
//=======================

//=======================
// PARAMETERS OF TASK
unsigned long waterdur = 60;
unsigned long waterdur2 = 60;
unsigned long trialdur = 1000000;
unsigned long sniffmaxdelay = 0;
unsigned long rchoice = INITIALGO;
unsigned long fvdur = 0;
unsigned long grace_period = 0;
unsigned long firststim = 0;
unsigned long iti = 5000;
//unsigned long lickfirst = 1;
unsigned long fvonset = 0;
unsigned long lickStartTime = 0;



//event to be transmitted back
unsigned int result = 0;
unsigned long paramsgottime = 0;
unsigned long starttrial = 0;
unsigned long endtrial = 0;
unsigned long firstlick = 0;
unsigned long firstcorrectlick = 0;
unsigned int no_sniff = 0;
unsigned long fvOnTime = 0;
unsigned long vialOnTime = 0;
unsigned long laserontime = 0;

// variables
uint8_t idx = 0, fv_routine_timer = 255, laser_routine_timer = 255, led_timer = 255;
uint16_t lickindex;  // lick index
int blocks;
bool trialdone = false, lastsent = false, enableblocks = false, maskon = false, ledMaskwFV = true,trialwait = false;
volatile bool trig_stop = false; bool beam1state, beam2state;
// state of the state machine
int code = 0, state = 0, trig_laser_multi_sniff = 0;
unsigned long temp1 = 0, inh_onset = 0, lastlickstamp = 0, lastlick1 = 0, lickcheckpoint=0;
int last_sniffndx = -1, cur_sniffndx = 0;
unsigned long nextpulsedelay = 0;
int treadmill_response_type = 0, rewards_given = 0;

//clean count iterates how many times the program will attempt to clean the mouse within a single session.
//lastCleanTime is the last time the cleaning iteration was started.

char buffer[128];
char *argv[8];
//bool received_params = 0;
//char laserdur[20], laseramp[20];

int step_num = 0;










void setup() {
  pinMode(LED_PIN, OUTPUT); // Green LED on the front
  pinMode(TRIGGER1, OUTPUT); // Pulse generator ch. 1 trigger
  pinMode(TRIGGER2, OUTPUT); // Pulse generator ch. 2 trigger
  pinMode(SOLENOID1, OUTPUT);
  pinMode(SOLENOID2, OUTPUT);
  pinMode(SOLENOID3, OUTPUT);
  pinMode(SOLENOID4, OUTPUT);
  pinMode(SOLENOID5, OUTPUT);
  pinMode(SOLENOID6, OUTPUT);
  pinMode(SOLENOID7, OUTPUT);
  pinMode(SOLENOID8, OUTPUT);
  pinMode(DIGITAL1,OUTPUT);
  pinMode(DIGITAL2,OUTPUT);
  pinMode(DIGITAL3,OUTPUT);
  pinMode(DIGITAL4,OUTPUT);
  pinMode(DIGITAL5,OUTPUT);
  pinMode(DIGITAL6,OUTPUT);
  pinMode(DIGITAL7,OUTPUT);
  pinMode(DIGITAL8,OUTPUT);
  pinMode(DIGITAL9,OUTPUT);  
  pinMode(DIGITAL10,OUTPUT);
  pinMode(DIGITAL11,OUTPUT);
  pinMode(DIGITAL12,OUTPUT);
  pinMode(CUE1, OUTPUT);
  pinMode(CUE2, OUTPUT);
  pinMode(CUE3, OUTPUT);
  pinMode(CUE4, OUTPUT);
  pinMode(CUE5, OUTPUT);
  pinMode(CUE6, OUTPUT);
  pinMode(CUE7, OUTPUT);
  pinMode(CUE8, OUTPUT);
  pinMode(ADC_PIN, OUTPUT);
  pinMode(DAC1_PIN, OUTPUT);
  pinMode(DAC2_PIN, OUTPUT);
  pinMode(TEENSY_PIN, OUTPUT);

  digitalWrite(LED_PIN, LOW);
  digitalWrite(TRIGGER1, LOW);
  digitalWrite(TRIGGER2, LOW);
  digitalWrite(SOLENOID1, LOW);
  digitalWrite(SOLENOID2, LOW);
  digitalWrite(SOLENOID3, LOW);
  digitalWrite(SOLENOID4, LOW);
  digitalWrite(SOLENOID5, LOW);
  digitalWrite(SOLENOID6, LOW);
  digitalWrite(SOLENOID7, LOW);
  digitalWrite(SOLENOID8, LOW);
  digitalWrite(DIGITAL1,LOW);
  digitalWrite(DIGITAL2,LOW);
  digitalWrite(DIGITAL3,LOW);
  digitalWrite(DIGITAL4,LOW);
  digitalWrite(DIGITAL5,LOW);
  digitalWrite(DIGITAL6,LOW);
  digitalWrite(DIGITAL7,LOW);
  digitalWrite(DIGITAL8,LOW);
  digitalWrite(DIGITAL9,LOW);
  digitalWrite(DIGITAL10,LOW);
  digitalWrite(DIGITAL11,LOW);
  digitalWrite(DIGITAL12,LOW);
  digitalWrite(CUE1, LOW);
  digitalWrite(CUE2, LOW);
  digitalWrite(CUE3, LOW);
  digitalWrite(CUE4, LOW);
  digitalWrite(CUE5, LOW);
  digitalWrite(CUE6, LOW);
  digitalWrite(CUE7, LOW);
  digitalWrite(CUE8, LOW);
  digitalWrite(LED_PIN, LOW);
  digitalWrite(ADC_PIN, HIGH);
  digitalWrite(DAC1_PIN, HIGH);
  digitalWrite(DAC2_PIN, HIGH);
  digitalWrite(TEENSY_PIN, HIGH);

  //=======================
  // prep ANALOG inputs
  analogReference(DEFAULT);
  //=======================

  //=======================
  // prep SPI for AD control
  startSPI();
  //=======================

  //=======================
  // initialize the SERIAL communication
  Serial.begin(115200);
  //Serial.begin(921600);

  //Serial.println("* Monitor System ready *");
  //=======================

  //=======================
  // initialize SERIAL for LCD
  Serial1.begin(19200); 
  Serial1.write(0x0c); // clear the display
  delay(10);
  Serial1.write(0x11); // Back-light on
  Serial1.write(0x80); // col 0, row 0
  Serial1.print("*CleanThresholding   Dewan Lab*");
  delay(20);
  //    Serial1.print(0x94, BYTE); // col 0, row 0
  //    Serial1.print("MODE 0");
  //=======================

  // Pulse generator communication
  Serial2.begin(115200);
  setupVoyeurTimer(); //setup and start ms timer (From: voyeur_timer_lib.pde) (THIS DEFINES TOTALMS).

  // setup buffer sizes
  setupBuffers(400,1,20,50);  //(ioFunctions)(unsigned int sniffbuff, unsigned int treadmillbuff, unsigned int lickbuff, unsigned int trigbuff)

  // recording of both sniff and velocity
  // first two args are analog channels' pins, 1 indicates ONLY SNIFF ON, 3 indicates both on.
  setupAnalog(0,1,1); 

  // start analog acquisition
  start_analog_timer(); //(ioFunctions).
  // start lick recording timer.
  // first arg. is the beam break pin, second is the amount of ms to wait. 0 = every ms
  startLick(BEAM1,BEAM2);//(ioFunctions).
  lickOn(3, 0); // 3 - turn on both lick pins, 0 is frequency (every ms). (ioFunctions).
  recordsniffttl = true;

  // Init done
  digitalWrite(LED_PIN, HIGH);
}

//===================================================================================================
void loop() {  //BREAKS TO HERE

  //===================================================================================================
  //================ State machine goes here===========================================================
  unsigned long timenow = totalms; //copy this to register from volatile.



  switch (state) {

  case 0: //waiting for initialization of trial
    break;



  case 1: // state was changed to 1 via controller (serial).
//    if((timenow-endtrial) < iti)  // wait for the inter-trial interval to be over (difference between last trial and the current time)
//      break;
//    else{
      vialOnTime = timenow;
      state = 2;
//    }
    break;

  case 2: // Wait for odor to reach max
    if((timenow-vialOnTime) < 900)  // 
      break;
    else{
      state = 3;
      digitalWrite(TRIAL_LED,HIGH); //Turn on Trial Light
      starttrial = timenow;
    }
    break;


  case 3:  // FINAL VALVE     If the final valve gets turn on, turn on the final valve for fdur time and mark the time

    valveOn(FINALVALVE);
    fvOnTime = timenow;
    digitalWrite(FVSYNC, HIGH);
    digitalWrite(ENV,LOW);
    
//    step_num = 40;
//    for (int i=0; i<step_num; i++)
//    {
//      digitalWrite(ENV_STEP,HIGH);
//      delay(2);
//      digitalWrite(ENV_STEP,LOW);
//      delay(2);
//    }
            
    state = 4;
    break;

  case 4:  //TRIAL TYPE.
    if((timenow-fvOnTime) < grace_period) // wait fo
    {
        break;
    }
        
    else{
          lickStartTime = timenow;  //mark start of lick time
          if(rchoice == INITIALGO) //Initial Go trials
              state = 5;
          else if(rchoice == GO) //GO TRIALS
              state = 6;
          else if(rchoice == NOGO) // NOGO TRIALS
              state = 7;    
     }
     break; 

  case 5:  // INITIAL GO TRIAL     

      //OPTION 1: Trial time ends with nothing happening
      if(timenow - starttrial > trialdur) { //Trial is over; nothing happened
      result = 5; // End Trial
      state = 10;
      break;
    }

      //OPTION 2: Animal Licks and receives water
      else if (haslicked(1,lickStartTime)){ //correct
      result = 1;
      valveOnTimer(WATERVALVE1, waterdur);
      firstcorrectlick = getLastLick(1);
      state = 8;
    }
    break;


  case 6:  //GO TRIAL      

      //OPTION 1: Trial time ends with nothing happening
    if(timenow - starttrial > trialdur) { //Trial is over; nothing happened
      result = 5;
      state = 10;
      break;
    }
   
  //OPTION 3: Animal Licks and receives water
    else if (haslicked(1,lickStartTime)){ //correct
      result = 1;
      valveOnTimer(WATERVALVE1, waterdur);
      firstcorrectlick = getLastLick(1);
      state = 8;
    }

    break;


  case 7:  // NOGO TRIAL
        //OPTION 1: Trial time ends with nothing happening ANIMAL IS CORRECT
    if(timenow - starttrial > trialdur) {
      state = 10;
      result = 2; //CORRECT REJECTION
      break;
    }

    // FALSE ALARM
    if (haslicked(1,lickStartTime)) { 
      result = 3;
      firstcorrectlick = timenow;
      state = 8;
    }
    break;

  case 8:  // Place holder to add time to wait for the end of the trial. Currently, trial is over after animal licks
    state = 10;
    break;


  case 10: // turn off everything, end trial, state 0
    valveOff(FINALVALVE);
    digitalWrite(FVSYNC, LOW);   
    digitalWrite(ENV,HIGH);
//    for (int i=0; i<step_num+20; i++) 
//    {
//      digitalWrite(ENV_STEP,HIGH);
//      delay(2);
//      digitalWrite(ENV_STEP,LOW);
//      delay(2);
//    }
            

    digitalWrite(TRIAL_LED,LOW); //Turn off Trial Light
    endtrial = totalms;
    trialdone = true;
    iti = 0;
    state = 0;
    break;

  }



  
  //===================================================================================================
  // CHECK SERIAL PORT
  //===================================================================================================


  if (Serial.available() > 0) {

    code = Serial.read();

    switch (code) {
    case 89: // stop execution
      state = 0;
      if(fvdur == 0) {
        valveOff(FINALVALVE);
        digitalWrite(FV_T,LOW);
      }
      Serial.print(3);
      Serial.print(",");     
      Serial.print("*");
      break;

      // all other codes are handshaking codes either requesting data or sending data 
    case 87:
      RunSerialCom(code); 
      break;

    case 88:
      RunSerialCom(code); 
      break;

    case 86:
      RunSerialCom(code);
      break;

    case 90:
      RunSerialCom(code);
      state = 1;
      paramsgottime = totalms;
      firstlick = firstcorrectlick = 0;
      starttrial = no_sniff = 0;
      laserontime = 0;
//      Serial1.write(0x0c);
//      delay(10);
//      Serial1.write(0x80); // col 0, row 0
//      Serial1.print('lick_training. Rewards: ');
//      Serial1.print(rewards_given);


      break;

    case 91:
      RunSerialCom(code);
      break;

    case 92:
      digitalWrite(SOLENOID1, HIGH);
      delay(5000);
      digitalWrite(SOLENOID1, LOW);
      break;
    }
  }
}

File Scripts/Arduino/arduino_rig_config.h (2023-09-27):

/*	Header of a behaviour board configuration and peripherals connected to it for an experimental rig.
 *  Have one configuration file per rig, unless same peripherals are connected to same positions in all boards AND all boards are identical.
 *  RIG: --REPLACE THIS WITH RIG NAME/NUMBER--
 *  # file should be placed in: 'C:\voyeur_rig_config\'
 * */
#ifndef RIGCONFIG_H
#define RIGCONFIG_H

#define LED_PIN   13   // Front panel green LED beside the USB port

// Pulse generator trigger pins (internal to behaviour box). Although 3 exist, only 1 and 2 have pulse outputs with current firmware.
// TRIGGER1 can be accessed if BNC between USB port and green LED is jumpered in the 'PGTRIG1' position
// Used to trigger a pulse, via the pulsegenerator microcontroller, on the PG1/PG2 output channels (BNC ports)
#define PULSETRIG1   4
#define PULSETRIG2   5
#define PULSETRIG3   6

// Valve solenoid pins. Connecting to the IDC header at the back of the behaviour box
// and into the terminal breakout box via ribbon cable.
#define SOLENOID1 29
#define SOLENOID2 28
#define SOLENOID3 27
#define SOLENOID4 26
#define SOLENOID5 25
#define SOLENOID6 24
#define SOLENOID7 23
#define SOLENOID8 22

// BEAM break sensor pins. Used to detect phototransistor state when a beam break circuit is connected to respective RJ9 port
// Can be used for detecting licks when a DC lick circuit is connnected to the RJ9 port, with the output of the circuit
// connecting to one of these pins. RJ9 port should be configured with the BEAM BREAK jumpers.
#define BEAM1     37
#define BEAM2     36
#define BEAM3     35
#define BEAM4     34
#define BEAM5     33
#define BEAM6     32
#define BEAM7     31
#define BEAM8     30

// CUE pins on the RJ9 ports. Used for turning CUEs, such as LEDs or Buzzers, ON/OFF.
// RJ9 port should be configured with jumpers on the CUE positions.
#define CUE1      45
#define CUE2      44
#define CUE3      43
#define CUE4      42
#define CUE5      41
#define CUE6      40
#define CUE7      39
#define CUE8      38

// Pins that connect the analog-to-digital and digital-to-analog converter chips to the Arduino.
#define ADC_PIN   49
#define DAC1_PIN  53
#define DAC2_PIN  48
// Pin that connects to the teensy microcontroller when installed in the behaviour board and jumpered properly.
#define TEENSY_PIN 47

// Digital Pins/Channels accessed at the BNC ports, when the BNC ports are configured in the digital mode via jumpers.
#define DIGITAL1  62
#define DIGITAL2  63
#define DIGITAL3  64
#define DIGITAL4  65
#define DIGITAL5  66
#define DIGITAL6  67
#define DIGITAL7  68
#define DIGITAL8  69
// Digital Pins connecting to the IDC header and subsequently to a terminal board via ribbon cable.
#define DIGITAL9  54
#define DIGITAL10 55
#define DIGITAL11 56
#define DIGITAL12 57
#define DIGITAL13 58
#define DIGITAL14 59
#define DIGITAL15 60
#define DIGITAL16 61

// Labels of digital output trigger pins (TTL) for debugging. Connect to BNC ports when the BNCs are configured as digital channels.
#define SNIFF_T DIGITAL6
#define FV_T DIGITAL5
#define LEDMASK_T DIGITAL7
#define LASER_T DIGITAL3

// Valve solenoids. Connect to terminal breakout board.
#define FINALVALVE SOLENOID8
#define WATERVALVE1 SOLENOID1
#define WATERVALVE2 SOLENOID2
#define WATERVALVE3 SOLENOID4
#define WATERVALVE4 SOLENOID5
#define CLEARVALVE SOLENOID7

// Digital pins found in the IDC header, which is connected to a breakout board. Access at breakout board.
#define STARTTRIAL DIGITAL10
#define LEDMASK DIGITAL11

#endif

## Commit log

2023-08-02 Upload all files
    [Cleaning Bottle Holder.stl, FanExhaustCover.stl, FinalValveMount.stl, Head Bar.stl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]
2025-03-11 Updated parts list as updating the key resources table in the publication is not straight forward; updated part numbers and purchase location for flowmeters; add CITATION file
    [STAR Protocol Parts List .xlsx]
